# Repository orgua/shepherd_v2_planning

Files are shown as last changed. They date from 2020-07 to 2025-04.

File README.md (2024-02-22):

# Shepherd V2 - Documentation of Planning and Execution




**Main Project**: <https://github.com/orgua/shepherd>

**Main Documentation**: <https://orgua.github.io/shepherd>

**DevLog-Documentation**: <https://orgua.github.io/shepherd_v2_planning/>

---

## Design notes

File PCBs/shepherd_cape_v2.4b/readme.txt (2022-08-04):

Umfang:

- 15 Baugruppen / PCBs 
	- wenn möglich 1 PCB Bestückung als Testsample und den Rest 2-3 Wochen später nach Freigabe
	- falls für die letzte Platine wenige Bauteile fehlen, dann gerne unvollständig bestücken
- 350 Bauteile, 50 unique
- einseitige Bestückung
- smallest part: 0402 
- smallest pitch: 0.5 mm
- only top layer populated
- Bestellung notwendig, nicht alle Bauteile konnten beigestellt werden (siehe Unten)

Platinenfertigung / Manufacturing Constraints:

- Designdaten befinden sich im Anhang
    - GerberX2-Datensatz
    - BOM und Packliste für SMD-Teile
    - Pick and Place Koordinaten für SMD-Teile
	- Assembly-Drawings
	- schematics und Platinenrendering

- PCB-Size ist 54.1 x 75.2 mm, 6 Layer
- Koordinatenursprung ist außerhalb des Boards, links unten

- Standard Eurocircuits / Betalayout Designrules
    - 0.15 mm Track Width
    - 0.15 mm Copper Clearance
    - 0.38 mm Edge Clearance
    - 0.35 mm Toolsize / non plated Hole
    - 0.25 mm Plated Hole (End-)Size
    - 0.125 mm Annular Ring
    - 2.54 mm Milling radius
	- beidseitiger Bestückungsdruck
- Stencil: Solder Paste Pads are optimized for a 70 - 110 um Stencil

- markings: 
	- Mech-15 contains assembly notes / Pick and Place 
	- marking origin of part: cross (+) on assembly notes layer 
	- marking pad 1 of ICs: chamfered edge and circle (assembly notes) and filled triangle (silk) 
	- marking cathode of diodes: "C" or chamfered edge (assembly notes) and filled triangle (silk) 
	- Mech-2 contains Top Part Designators 

BOM / Bestellung:

- BOM hat rechts Spalten für Info über beigestellte und fehlende Bauteile
- Bauteile können durch den eigenen Bestand ausgetauscht werden, falls es den Prozess vereinfacht
- fehlende oder nicht ausreichende Bauteile bitte Nachbestellen

Difference in B-Version of v2.4

- adapt to mouser-stock 
	- Pitch: avoid .35 mm , now it's >= 0.5 mm
	- Solder Mask Sliver: now safer > 0.2 mm

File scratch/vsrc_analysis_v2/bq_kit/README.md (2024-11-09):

# Characterizing the BQ25570 Eval Kit

## Setup

Components described from front to back

- Elgato Key Light in white Light Box
	- controllable by percent-value
    - first run: 5 %, 10 %, 15 %, 20 %
    - lowest: 3 %
    - second run: 4, 6, 8, 10, 12, 14, 16, 18, 20, 22
- Solar cells in same box, exposed to the LEDs
	- model: TBD
    - VOC-MAX ~ 3.18 V
- BQ25570 with said solar cells as input
	- BQ25570 Eval Kit (Modded as described below)
- resistive load on output of buck-converter
	- Open Circuit (OC), 1k (cherry-picked, spot on)

## Measurements

- ivcurves of solar cells, recorded with shepherd harvester @ different light levels
- Saleae Logic Pro 16 (2MOhm Impedance) was used to record analog pins of BQ-IC
    - 31 kHz sampling rate 
	- V_IN - output of solar cell, input of BQ
	- V_BAT - (==V_STOR) voltage over storage capacity on Eval Kit
	- V_Out - output of buck-converter, input of load
- BAT_OK signal was recorded digitally by the logic pro
	- BAT_OK is also enable-signal for buck-converter of BQ

# Changes to the BQ-Eval-Kit

- lowering the VOC of the solar cell -> one cell, not two in series
- adjust the V_Bat over-voltage limit to ~ 5.25 V (5.5 is the theoretical max)
  - the capacitor is rated for 6.3 V
  - VBAT_OV = 3/2 * VBIAS * (1 + R1/R2), VBIAS = 1.21 V
  - 4.18 V setup: R1 = 7.5 M, R2 = 5.76 M -> EVM-Default
  - 5.00 V setup: change R1 = 10 M -> violates BQ-Req that R1 + R2 < 13 M
  - **5.22 V setup: change R2 = 4 M (preferred, 2x 2M)**
- adjust hysteresis of Bat_OK to 4 to 4.5 V
  - default: 2.79 V to 2.99 V for BAT_OK = ON
  - BATOK-PROG = VBIAS * (1 + R7 / R8)
  - BATOK-HYST = VBIAS * (1 + (R6 + R7)/R8)
  - default: R6 = .887 M, R7 = 6.98 M, R8 = 5.36 M
  - 4.03 to 4.38: change R8 = 3 M
  - **4.03 to 4.43: change R6 = 1 M, R8 = 3 M (preferred)**
  - 4.03 to 4.83: change R6 = 2 M, R8 = 3 M (showed some unwanted effects)
- enable output with BAT_OK (enable JP6)
- directly connect V_STOR = V_BAT (bridge the Mosfet)

- Setpoint: on-off-behavior should be present
  - double solar cell @ LED900mA can produce 4mW, so one cell should bring 2 mW
  - 1 kOHms at 1.8 V draw 3.2 mW (most interesting)
  - 100 Ohms at 1.8 V draw 32.4 mW

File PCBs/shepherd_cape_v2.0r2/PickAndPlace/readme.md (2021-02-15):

InCircuit 
Wanted format: http://wiki.in-circuit.de/index.php5?title=Format_Maschinendaten

- Bestückung von 30 PCBs, einseitig, alles SMD (minimal 0402, QFN, nichts exotisches)
- PCB-Maße sind 55x75 mm mit zusätzlichem umlaufenden Nutzen, 10 mm
- 292 Bauteile, 40 Unique (volle Version)
	- 235 Bauteile, 40 Unique (ohne Recorder / Linker Shield + Teile Links davon)
- Koordinatenursprung ist nicht die linke untere Ecke der Platine, sondern 11.176 mm nach links verschoben
- Bauteile werden von uns gestellt, leider nicht im Reel
- R/C-Standardbauteile können gerne ersetzt werden durch Ihren Bestand, falls die bestehenden Reel wirtschaftlicher verwendet werden können als unsere Bauteiltüten 
   - falls es Toleranz-Anforderungen gibt, sind sie bei Value notiert
   - 173x 0402-Bauteile könnten in Frage kommen

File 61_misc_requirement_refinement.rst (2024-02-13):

Requirements Refresh / Refinement 2022-06
=========================================

(rough version)

- more focus on a general testbed for the Internet of Things, especially:
- GPIO Monitoring -> higher min sampling frequency / guarantees
	- nRF and MSP430 have 16 MHz baseclock -> same region would be nice
	- chip-rate of 2 MChip/s,
	- 200ns per loop == must, 150 ns == nice, more welcome
	- idea: state-machine triggered sampling with max window size (example: target uses one pin to trigger sampling for 50 ms)
- UART Monitoring (RX from Target-Side), min 461 kBaud, better 922 kBaud (1MBaud maybe easier)
	- software defined, linked with GPIO-Monitoring
	- timestamp with 1ms-resolution is enough, whole line, start of transmission
	- more detailed timestamps are often embedded in message itself
	- document wrap (if needed), for someone that uses no \n\r, OR
	- OR user-defined wrap-symbol
	- test for ascii control chars (storage in h5 and csv-file) -> or document forbidden chars
		- also base64, 85, 91, or raw
	- continuous stream should also be functional (1MBaud, long duration, creates 10Mbyte stream currently -> might be a problem) -> specify max rate if not possible
- actuation (like UART-Sending):
	- telnet seems not useful (tests can run at night, )
	- top-feature: script on observer with additional logic would be nice (read and write gpio / uart)
	- nice-feature: config-file with time-based send-commands
	- min feature: gpio-actuation per PRU, synced
	- idea: state-machine preload, without reads during run,
- lower sampling bounds should be guaranteed and known -> avoid spurious phantom signals
- Sync-Error should be lower than Clock of GPIO-Register of target

     - Example: 1 / 16 MHz -> 62 ns

- GPIO Actuation, set predefined pins, precise between nodes, resolution can be rather low (100 kHz more than enough, even 10 Hz could be enough), parameters:

    - t_offset (since start of measurement)
    - node(s)
    - GPIO(s)
    - State

- GPIO Actuation for Live View could be beneficial (users can check if system is alive, but what else?) (only nice to have)

Thoughts on Feasibility
=======================

GPIO Monitoring

- with constant voltage (only current-monitoring, no virtual source model) one PRU-Core would be idle -> custom firmware
- PRU0 handles monitoring el. current, actuating GPIOs, Sync timebase, exchange data-buffers
- PRU1 handles only GPIO-Monitoring -> busy waiting

UART Monitoring

- current design routes UART to ARM controlled Pins (Linux) and PRU (GPIO Monitoring, discrete timestamped Events)
- Linux UART RX will be tested -> we are currently stuck at kernel 4.19 but have to switch to 5.10+ eventually
- for PRU monitoring the dedicated section applies

Sync-Error

- there is still a low frequency with unknown origin (~ 0.2 Hz)
- current limits are hard to improve
    - error between nodes: +- 400 ns abs, q95% ~ +- 200 ns
    - error between local triggers: ~ +- 120 ns abs, q95% ~ +- 50 ns
- tbd: deployed cisco-switch in TUD has layer 3 routing and >doubled spec -> could improve sync

TODO
====

- implement enablers / general improvements

    - decouple GPIO-Ringbuffer from IV-Stream-Buffer -> size constraint of 16k Events per 100 ms
    - current buffer-swap implementation is not optimal, takes too much time and should be replaced by a big ring-buffer -> makes mutex between PRUs redundant

- test UART RX with kernel 4.19 / 5.10 with 461 and 922 kBaud
- fork PRU-Firmware with focus on GPIO-Speed

    - test capabilities

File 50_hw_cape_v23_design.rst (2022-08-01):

Shepherd Cape v2.3
==================

Changes Done for v2.4
---------------------

- Power Analog-Switch U30 from BB 3V3
- stabilize ADC with 22 pF at Input -> 60 kHz Fc
- stabilizing 1kOhm for VIOBuffer
- decide if rec & emu should be combined
    - more complex design
    - always complete package
    - reduced cost (~ 3*9 €)
    - emu gets voltage-measurement for free
    - -> no for now
- ADC seems to act up sometimes after sheph-EN -> test in PRU, reenable a couple of times -> seems to be fixed with EN
- Pwr-by-BB does not work with current cape-revision -> just add a switch?
    - switch for input power, 1 A, 5V Switch: https://www.mouser.de/ProductDetail/Dialog-Semiconductor/SLG5NT1594V?qs=sGAEpiMZZMtxrAS98ir%252BsxAQ5ATuKOGcAYPhn0zy8SaYiCqL8FxMXA%3D%3D
    - test shows that the unpowered watchdog is responsible -> add another diode to also power WD from BB 5V OR power diode directly from middle-pad of 2-WayJumper
    - tests still show unreliable starting-behaviour when BB-Pwrd (start on second try), hints at trouble with big coil & Cap -> also implement the switch
- remove overvoltage-protection, due to space constraints
- ditch LSF-LevelTranslator, use 74LVC2T45DC,125 with directed pairs
    - 74LVCH2T45GT, holds, 1.0 * 1.9 mm Package: https://www.mouser.de/ProductDetail/Nexperia/74LVCH2T45GT115?qs=jquClx72t9BCfx5QcUZHzg%3D%3D
    - 74LVC2T45GN, without hold, 1.2 x 1.0 Package
    - 74LVC2T45GS, without hold, 1.35 x 1.0 Package -> cheaper, more available
    - 4x100k-PU Array https://www.mouser.de/ProductDetail/YAGEO/YC124-JR-07100KL?qs=o9qB%2F%252BVTi4WdZhClKs2MsA%3D%3D
- programming biDir Pins
    - var1: skip leveltranslator and force 3v3 logiclevel, direct connection with analog Switch
    - *var2*: that one pin tdio must have a dir-pin -> hard if PRU-Pins needed
    - var3: still use slow LSF0104 for programming pins (try TI-Version for a change)
    - -> var2 is preferred if sys-gpio is working for programming, (YES, it is)
- GPIO to target, 7x GPIO, 2x UART (rx,tx), BAT_OK (tx)
    - how many gpio should be with variable direction? 2x2 rxtx, 5 static rx? ->
    - static-Dir TX: CLK1, TMS/CLK2, BATOK -> 2 x 2 CH Translator
    - static-Dir RX: UART-RX, 4x GPIO, -> 3 x 2CH-Translator
    - BiDir: TDIO1, TDIO2, UART-TX, 3x GPIO (4 Dir-Controlling Pins, 2 for programming, 2 for tx&GPIO and 2-4xGPIO)
        -> could be bundled in TDIO/GPIO-Pairs for a 2 x 2CH-Translators (NO)
        - if possible don't share Dir-Pins between programmer / gpio
- possible extension of target port
    - programming pins are exclusive and don't have to be recorded/monitored -> free pins should be used for additional gpio
    - a second target (with option of programming) would help for some usecases (MSP430 + nRF-Radio)
    - var1: analog switch on target-pcb for programming lines controlled by one of the gpio (exclusive or could still be used as gpio)
    - var2: analog switch on cape, 2x2 programming lines on target-port, also allows JTAG
    - var3: intermediate uC on target-pcb for programming targets talking with BBone over programming lines (very custom solution but cape is left untouched similar to var1)
    - -> Var2 preferred
- WD-Wake needs longer Pulse
    - currently 20ms High-Pulse gets inverted, but tests show that > 130 ms are needed
    - var1: diode + RC-Filter could widen the Pulse
        - wake-pin supplies 1mA max
        - SIM: 100 nF / 1 M -> 150 ms > 0.5V (On for MOSFET)
        - SIM: 1 uF / 1M ->  >>1s > 0.5V
    - var2: a single capacitor after the mosfet could suffice
        - BB-Schematic only shows a pull-down button
        - TPS65217C, PB_IN, Pin25, internal 100k PU
        - SIM: 1 uF from BB-START to GND shows 100ms delay for signal rise to 2.0V -> sums to 120 ms
            - ~ 64ms in real test
    - -> Var1 preferred, less dependant from BB-Design-Changes
- PUs on sys-side should also be powered by BB 3V3
- New Connector, 4x Pwr, 4x Prog, 10x GPIO -> 18 Pins -> 2x9 Connector
    - info1 -> BB outer width is 54 mm -> 27mm per module
    - info2 -> BB width between headers is 43.2 mm -> 21.7 mm per module
    - var1: remove mounting-holes and allow 2.54mm Connectors (2x 22.2 mm width)
    - var2: switch to smaller 2mm Connector, ~18mm width
    - -> var1 preferred
- GPIO-PUs increase to 100k
- combine shield-pads for EMU & REC
- change Analog switch to microbump-version 863-NLAS4684FCT1G
- change back vias from 550/200 to 600/250
- add more decaps for level-translators
- Remove dedicated harvest-led -> use pru0-LED for that

Changes still Open
------------------

- which rails would benefit from big Caps?
- emu-shunt should be stabilized with > 500 nF (and probably the others too)
- additional big Caps on Main-Rails
- Resistor Arrays?
    - 4x 100k https://www.mouser.de/ProductDetail/YAGEO/YC124-JR-07100KL?qs=o9qB%2F%252BVTi4WdZhClKs2MsA%3D%3D
    - others1 https://www.mouser.de/c/passive-components/resistors/resistor-networks-arrays/?resistor%20values=100%20kOhms&instock=y&sort=pricing
- Beta Tuning:
    - additional 1 nF Cap on Feedback LP, both paths
    - remove 100 nF parallel to shunt
    - give recorder equal layout
- optimize filters with noise-metrics
    - possible tradeoffs: speed of voltage-transitions, compensation of analog switch resistance
- finalize hardware (WD, filters, GPIO-Speed, current bugs)
- test harvesting-target
- get target naming A/B/1/2 straight. it is target 1/2 from now on!
- find reason for 2.3mA Offset
- diodes for coils if needed
- LED of PRU: dedicated pwr_good / harvesting on silkscreen

Trouble with v2.3c - manual P'n'P
---------------------------------

Fixed in v2.3d

- better comments for parts, U- , L-, R-.... T-
- SLG5... 4pin-mini-package, improve pin1-point and pad-layout should be hinted at ->
    - also longer pads,
- optimize NLAS-BGA, silk-lines, maybe extend corner-pads, peek over ic-edge or add right angles in copper
- 74LV LVLTrans - longer pads, at least the 4 corner ones -> maybe one package larger
- 0402 pads closer together
- u14 pads further apart
- the 3 new ICs -> maybe back to larger package?
    - 74LV as QFN, end-of-life: https://www.mouser.de/ProductDetail/Nexperia/74LVC2T45GM125?qs=sGAEpiMZZMtZ661ya8CuXWImkGMxfA6p9uS%252BIOJA%2FTA%3D

- 1 C tombstone (below emu, above u19)
- level-trans seem to be shorted (densest pad-layout)
- some ICs are shorted -> old paste

Additional Parts
----------------

- 22pF for Emu-ADC
- 1k Ohm VIO-Buffer
- 9 74LVC2T45GS -> 2CH LevelTranslators
- 1x SLG5NT1594V -> 1A Power-Switch
- EN_CONV: R 10k, C 1uF
- WD: 2x NSR05T30XV2T5G, R 100k, C 1uF
- LVL-Trans: >20x 100k, 5x 1uF
- AnalogSwitch: 9x 863-NLAS4684FCT1G
- pinheader 2x18, 2x 649-1012938191801BLF

Parts not needed anymore
------------------------

- OVP: 2x FB 0603, C 22 uF, R 10 k, Mosfet BSH105, Diode NSR05T30XV2T5G
- WD: R 10k

Target Pin Design
-----------------

- GPIO 0            - dir1-pin / rxtx
- GPIO 1            - dir1-pin / rxtx
- GPIO 2            - dir1-pin / rxtx
- GPIO 3            - dir1-pin / rxtx
- GPIO 4            - always RX
- GPIO 5            - always RX
- GPIO 6            - always RX
- GPIO 7 - uart rx  - always RX
- GPIO 8 - uart tx  - dir2-pin / rxtx
- BAT OK            - always TX

- SWD1 CLK - jtag TCK   - always TX
- SWD1 IO  - jtag TDI   - pDir1-pin / rxtx
- SWD2 CLK - jtag TDO   - always TX
- SWD2 IO  - jtag TMS   - pDir2-pin / rxtx

PinChanges from prior Version v2.2 to v2.3
--------------------------------

see `./PCB/beaglebone_pinout_concept.xlsx` for more details

Changes

- p8-27 was pru-gpio4, now pru-uart-tx
- P8-39 was pru-gpio2, now pru-gpio6
- P8-40 now pru-uart-rx
- P8-41 now pru-gpio4
- P8-42 now pru-gpio5
- P9-17 only naming, swd1_clk
- P9-18 only naming, swd1_io

New

- p8-31 / 32 now used for io-dir
- p8-33 sw_swd2_io
- p8-34 sw_gpio6
- p8-35, 36, 37, 38

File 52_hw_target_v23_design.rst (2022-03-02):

Target with nRF52 and MSP430
============================

Changes still Open
------------------

- new Target-Port
- wider PCB allowed, BB-Heigth is 54.1 mm -> half is max 27 mm
- TargetPCB: are there constraints or feedback for the MSP430 + NRF - Combination
    - Which IC would you prefer?
    - example-schematic for the combination available?
    - IC interconnect: SPI (4 Lines), 2+ handshake-lines (Project Squeece)
    - Target-Connector-Gpio access for both uCs?
    - TODO: use nRF TRCDAT0 / P1.00 / on Target header
    - Github / squeece
- target -> add target powered LED to burn away energy (or use second LED for that purpose)
- nice to keep similarity to DK, but not a must
- Squeece Pin-usage
    - C2C CLK,  P0.13,  P1-6_UCA0CLK
    - C2C MOSI, P0.12,  P1-4_UCA0TXD
    - C2C MISO, P0.16,  P1-5_UCA0RXD
    - C2C CS,   P0.15,  P1-7_UCA0STE
    - C2C GPIO, P0.14,  P2-7_CAP3
    - nrf-gp0   p0.17
    - nrf-gp1   p0.19
    - nrf-gp2   p0.28
    - nrf-led   p0.29
    - msp-gp0           P2-1_XIN
    - msp-gp1           P1-1_UCB0CLK
- MSP430 Variants
    - MSP430FR2433IYQWR -> BGA-Version, 16 kB FRAM
    - **MSP430FR5964** with 87 Pins, 256 kB FRAM -> there is an 48 PinVersion FR5994, even 59941 is ok
    - MSP430FR5992IRGZR , 48 Pins, 128 kB FRAM
    - or MSP430FR2155 with 32 kB and 48Pins and 32 MHz -> PinCompatible?
    - SPI to Target, seconds SPI to nRF
    - prepare to equip both crystals (HF, LF)
    - eine der eUSCI Schnittstellen (sind beim MSP hart verdrahtet) soll richtung BB gehen. Und der eine pin davon (z.B. UCA0RXD/UCA0SOMI) muss auf BB richtungsschaltbar sein.
- msp430
- shared pins are working fine on squeece, ~ 10nA draw on high impedance
- add star-resistors
- programmer - compensate lines with passive network

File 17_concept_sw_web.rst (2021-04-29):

Concept - Software - Web Interface
==================================

MetaInfo
--------
- derived from requirements, concept_shepherd and concept_meeting_notes

Design-Features
---------------
- Privacy is a features - avoid personal data (OAuth, ActiveDirectory)
- usage per website & API
- 1 experiment at a time, no concurrency

Functions
---------
- user-management
    - permission
    - role management
    - groups (share datapool)
    - Quota (data is linked to user and deleted with the account)
- authentication via external service like OAuth (i.e. Github) (if possible)
- Upload user provided data
    - Harvesting- / Energy-Traces, -traces, IV-Curves
    - regulator / converter-definition
    - Target-Firmware
    - user-scripts (sandboxed, limited resources (cpu, ram, storage), only limited libs allowed, limited user, lowest nice-level)
- Scratch-Area for experimentation-results (or DB)
- integrated pre-tests for measurement: test for plausibility, pre-run in software (abstract virtual hardware)
    - link in python code of shepherd project
- scheduler for measurement, time to prepare and follow up (data transfer, conversion, compression, ...)
- results downloadable by user, for a certain time (no hording)
- feedback via e-mail - measurement start, data available, error, shortly before deletion
- (optional) grafana-visualisation
- documentation and instructions
    - landing page
    - "what is that thing in my office"
        - clarify use and capability of the boxes (so people sharing an office with the testbed don't freak out)
    - where find what
    - FAQ
- Testbed-Status
    - structure
    - last seen
    - handle lockups (power-cycle)
    - keep testbed alive for a limited time (otherwise it will go to sleep / power down)
- collecting of logs (temp, ram-usage, cpu-usage, time-sync, ...)
- Web-Framework (some points are redundant)
    - user-management (roles for admins and users)
    - experiment-management, configure and control, add data (see below)
    - experiment-scheduling, calender (set active, start-time, duration)
    - data management / quota (retrieve / delete recordings)
    - authentication via external services
    - E-Mail notifications
    - testbed status, topology
    - (optional) grafana visualisation of recorded data
    - (admins) server status, quota, testbed control
    - documentation and instructions
    - target-management (specify slots of nodes)
    - (optional) benchmark-management (post-scripts)
- live-view -> lower prio

Implementation
--------------
- possibly python based (django vs flask, big vs small)
    - django offers the most, is flexible, modular and easy to extend
        - admin-interface
        - authentication (also oauth client), accounts
        - session-management
        - sub-websites with html-templates
        - -> security seems to be OK, attach surface is big, but >v3.0 seems to be mature
    - flask is a microframework, offers minimal attack surface and seems perfect for the python REST API
- basic implementation could be similar to https://github.com/fkt/36c3-junior-ctf-pub (web-interface for a ctf, that didn't get compromised)
- API: rest
- (prio) allow scripted workflow -> yaml -> rest ->
    - this could also be the base for the web-page-interface
- Database
    - influxDB or
    - timescaleDB
    - postgreSQL
- MessageSystem
    - Protobuf
    - RabbitMQ
    - RPC
- visualisation, analysis -> dash?
- option to sample down

DB Decision
-----------
- needed:
    - 30x 100k Inserts of timestamp (8B), node_id (1B), voltage (4B), current (4B)
    - -> 3M Inserts of >=17 Bytes -> 3 GB / minute
    - can happen locally or remote, concurrently is fine
- main bottleneck:
    - databases with timeseries do not seem to have a low level api for insertions, interface is ascii and needs parsing
    - (solution) low level api (raw data, shared mem, ...) -> there are possible formats like::
        - BSON -> MongoDB
        - UBJSON -> TeradataDB, Wolfram (no use for us)
        - apache avro -> Apache Spark SQL
        - JSONB -> Postgresql, but they say: "JSON is faster to ingest vs. JSONB"
- Timescale DB vs Influx -> influx seems to dominate with fewer devices <= 100
- timescale: SQL, robust, based on postgreSQL, time series, relational, various datatypes
    - looks more professional, but like influx they want to sell
    - presetup hard to script
    - 1M insert/s are considered excellent, i landed at ~60k with one remote connection
    - no low level api available, but some SQLs allow to load from file (csv)
- influxDB2:
    - inserting 200s data takes ~ 190s (1 node), with almost no load on VM or system
        - -> makes 108k/s inserts from one node
        - marketing documents say the insert-rate of free-database is good for ~ 250k/s
        - is it artificially limited or is it another invisible bottleneck?
    - ram usage seems to be ok << 1 GB
    - query's with ns resolution can get very slow. ~3s for averaging windows
    - influx can almost naturally import hdf5, numpy-arrays, pandas Dataframes
    - dataexplorer shows plots only windowed, smallest window is 1s (may be unimportant)
- elastic + logstash, search engine,
- redis, key-value store
- mongoDB
    - allows usage of BSON instead of JSON

DB-Bypass
---------
- measurement-data could be stored directly on the server
- each measurement is stored in a separate folder, named by hash or timestamp
    - it contains config data, logs and results
- file-references are inserted into a DB
- metrics for benchmarks or competitions could be generated by a user-script
    - pandas or numpy, as a fast cPython convenience, allows powerful oneliners
    - these metrics could be displayed on the website as a condensed result
    - these metrics could also be used for some kind of leaderboard
- a downsampled dataset (1 kHz?) could be fed into a database for semi-live analysis / observation
- a full-res dataset could be fed into the database afterwards but would mean a longer blocking time between measurements

TODO
----
- try payed db-vm (influx)
- compare elastic against influx, no support for nanosec?
- benchmark server (disks / ram)
- offer predefined energy-patterns (on/off, diode, different converters (boost, buck/boost))
- design-choices for later
    - does shepherd need databases for immediate (deep)analysis of result
        - alternative: provide post-scripts that filter data for key-parameters (benchmark-management)
    - data hording or economical use of space?
    - what else ?????

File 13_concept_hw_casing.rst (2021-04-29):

Hardware Casing for Nodes
-------------------------

Constraints
-----------
- nodes can vanish, wander
    - fixate
    - keep inconspicuous (under desk an option?), make it look official / blend in
- nodes can freak out new people in the same office
    - must look professional, official
    - be transparent about the function (inform current people in office, but also use sticker to provide a FAQ-Website
- must support cooling (direct sunlight, proximity to radiator)
    - convectional cooling would be the easiest
- must contain
    - BBone with shepherd Cape (75 x 55 x 25 mm)
    - POE-Converter (81 x 55 x 25 mm)
    - Target nodes (20 x 30 x 4 mm) - orthogonal on capelet or in direction of longest edge of capelet)
    - < 20 cm Network cable
    - power-connection
    - USB-Stick (45 x 20 x 9 mm)
    - opening for one RJ-45-Socket
- must be transparent to RF
- input Marco:
    - open and transparent is fine and wanted (!)
    - boxy is ok
    - preferable hard mounted to the wall with just one cable attached

Layout
------
- flat on one level
    - X: 75 + 45 + 30
    - Y: 55 + 55
    - Z: 25
    - 150 x 110 x 25 (412 cm²)
    - pro: clean,
    - contra: harder to cool, less optimal RF-performance (antenna near to ground)
- Stacked
    - X: 75 + 45
    - Y: 55
    - Z: 25 + 25 + 30
    - 120 x 55 x 80 (528 cm²)
    - pro: more boxy, would better fit ontop of the cable canal
    - contra:

Solutions
---------
- 3d-Printing
    - flexible and custom case
    - way to expensive for 30 Nodes
- Casing in laser-acrylic or plywood
    - solid, custom
    - may look also unprofessional, like a building kit
    - design without screws -> https://hackaday.com/2013/02/27/acrylic-enclosures-use-integrated-clips-to-do-away-with-fasteners/
- off-the-shelf case with custom front
    - can look professional
    - you have to take what the market offers
    - way around custom front is: just include an opening for the cable with a gasket (or right there where two halves meet)

Off-the-shelf Cases
-------------------
- flat (25-35 height, 150-183 length, 110-135 width)
    - https://www.mouser.de/Enclosures/_/N-5g3o?P=1yzti4fZ1yzxi2vZ1yzu1qgZ1yzxiszZ1yzu1na&Rl=5g3oZer8qZ1z0wu34Z1yzsnvlSGT5g3oZer7lZ1yzxi96Z1yzxi5vSGT
    - hammond 1599TABMBK / GY, 28 x 135 x 169 mm with custom cover, hardware can be mounted inside with laser-cut brackets
        - https://www.hammfg.com/electronics/small-case/plastic/1599tab
    - hammond 1557FGY, 160x160x45, no option for cover
        - https://www.hammfg.com/electronics/small-case/plastic/1557
    - hammond RM2055S
        - https://www.hammfg.com/electronics/small-case/plastic/rm2
- stacked (120-140 length, 55-75 width, 80-125 height)
    - https://www.mouser.de/Enclosures/_/N-5g3o?P=1yzu1tfZ1yzu1f6Z1yzu1ggZ1yzsn9pZ1yzoes7Z1yzxin2&Rl=5g3oZergvZ1yzu1ffZ1yzxigsSGT5g3oZer8qZ1y8pz55Z1z0wu4tSGT
    - Bud PTS-25312-C, 5.12x2.76x3.15"
    - Hammond 1554G2Gy, https://www.hammfg.com/part/1554G2GY
    - hammond 1555, https://www.hammfg.com/part/1555G2GY
    - hammond RP1150C, https://www.hammfg.com/part/RP1150C
    - hammond rp1155, https://www.hammfg.com/part/RP1155

Favorite 1599TABMGY
-------------------



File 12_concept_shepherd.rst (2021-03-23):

Shepherd - Concept
==================

Overview
---------
- (mobile) testbed for batteryless IoT
- observer-nodes for an IoT-Target
- works autonomous or time-sychronized with a network backplane
- "software defined power source", emulation of
    - harvesting source (pre-recorded, simulated)
    - regulator / converter - circuit
    - intermediate storage-capacitor
    - "software defined" is largely true, but changing basic behaviour needs a deep dive into PRU-Code
- allows to experiment with emulated spatio-temporal energy availability
- recording of energy-traces -> key-parameters like current-drain and (virtual) capacitor-voltage
- additional functionality: recording of harvesting sources (not part of testbed)

Nodes
-----
- embedded linux board with shepherd-cape
- time critical code runs on two real-time processors
- two targets-ports are available
    - both can be supplied with individual voltages, only one is current-tracked
    - general purpose IO, target selection independent from power-supply-selection
    - separate 3V3 line
- bidirectional GPIO on 10 channels, 2x2 lanes are currently reserved for SWD / Spy-by-Wire, UART
- Targets (currently planned)
    - nRF52840
    - MSP430

Testbed
-------
- 30 Nodes on one floor in a university office-building
- nodes powered via POE
- (optional) one PTP-Masterclock, Node with GPS
- 1 Ubuntu Control-vServer, 10 TB of additional Storage
- 1 experiment at a time, no concurrency
- Web-Framework
    - user-management (roles for admins and users)
    - experiment-management, configure and control, add data (see below)
    - experiment-scheduling, calender (set active, start-time, duration)
    - data management / quota (retrieve / delete recordings)
    - authentication via external services
    - E-Mail notifications
    - testbed status, topology
    - (optional) grafana visualisation of recorded data
    - (admins) server status, quota, testbed control
    - documentation and instructions
    - target-management (specify slots of nodes)
    - (optional) benchmark-management (post-scripts)
- user-provided data (experiment management)
    - (optional) energy-traces, IV-Curves
    - regulator / converter-config
    - target-firmware
    - (optional) python userspace script that interacts with gpio / serial

Technical details
-----------------
- Beaglebone Green with 1 Core for Linux and heavy use of PRU for low-latency code
- target-voltage 0 to 4.5 V, max 50 mA per Target
    - 16 bit DAC, LSB results in 76 uV
    - 100 kHz sampling rate, jitter max +- 90 ns, 95% Quantile is 60 ns
    - 18 bit ADC, LSB results in 19.1 uV or 191 nA
- speed of voltage-drive
    - DAC has 0.75 V/us slew and 7 to 10 us settling (error < 0.x %)
    - OpAmp has 5 V/us slew
    - following Lowpass has corner-frequency of 16 kHz
    - 10 kHz on-off-patterns should be well in range
- low noise & high precision design for analog frontend
- 10 shared GPIOs with system
    - bidirectional level translation works from ~ 1.3 to 5 V
    - line is driven by PUs, always matched to target-voltage (low power usage)
    - recording: sampling rate is asynchronous, between ~ 1 to 5 MHz
    - data throughput untested, but edges look fine for > 1 MBaud
    - leakage during operation < 2 uA from target-side
    - gpio can be turned of, < 10 nA leak from target-side
- data-rates
    - 1 min ~ >= 54 MiB of measurement data (more with heavy GPIO actions)
    - 1 Hour, 30 Nodes -> 100 GiB uncompressed (hdf5)
- time-synchronization
    - in linux via PTP,
    - chip-select edge of two test-nodes have a maximum jitter of about +- 300 ns, 95% quantile is 160 ns
- external watchdog for wakeup / restart on
- network
    - Server has 10 GBit Link to Switch
    - Nodes have 100 MBit Link to Switch

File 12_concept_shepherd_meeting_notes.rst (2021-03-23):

Learnings, with Pitfalls and (possible) Solutions
=================================================
- notes from meetings with creators of established testbeds
- significance for shepherd is incorporated

Server
------
- have an upgrade path
    - currently TUD/ZIH offers vServers and plenty of Storage from its datacenters, can be changed, expanded
    - current server: 2 Cores, 4 GB RAM, 50 GB local Storage, 10 TB network storage
    - vmware-tools have option to set cores and ram to 64 (for privileged users)
- avoid windows OS
- splitting servers can be an option (storage with message broker, web-interface, computing)

Data-Management
--------------
- database (not a must)
    - allows easy analysis of data
    - immediate access is nice! real time or direct access for devs (even jupyterNB)
    - needs lots of RAM
    - easiest interface is a socket with json-interface -> inefficient for embedded systems, can often be avoided
    - can produce downloadable data on the fly (at least csv)
- hdf5 / raw-data
    - needs more custom code
    - analysis not available right away
- database-choices
    - influxDB allows nanosec-timestamps as a series
    - postgreSQL works for weeks
    - timescaleDB, inlux competitor, seems to scale better with large number of devices (>1000)
- leave headroom, node-resources can easily become the bottleneck
    - using third party libs is always a good idea, but can come with performance penalties
    - usually compute-load can partially be moved to server
    - there are often performance optimized forks of established libs around (if needed)
- established ways / libs to stream data out
    - protobuf (can be slow for python)
    - rabbitMQ / kombu
    - RPC
- is privacy is feature? avoid personal data (OAuth, ActiveDirectory), make recorded data private (even only delete-access for web-admins)
- grafana seems to have trouble with big datasets

Nodes
-----
- lockups -> powercycle
    - we (shepherd) may not have the chance to control POE
    - there is an external watchdog on the shepherd-capelet
    - there should also be a watchdog integrated in cpu (untested)
    - until now i (ingmar) had no trouble with the nodes, software base seems solid
- heat through sun, radiators, enclosure
    - degrades cpu, storage
    - BBone stays below 40 deg, case will support convectional cooling
- avoid storage without wear-leveling
    - sd-cards are not up for constant data-storage (and industrial SLC-Versions are expensive)
    - large usb-sticks tend to have wear leveling -> ours probably hasn't
    - BBone has eMMC for the linux image, support for wear leveling is unclear
    - filesystems like F2FS have a software-based wear-leveling
    - possible solution
        - keep results in ram (avoid local storage bottleneck) and stream to server
        - use usb-stick for local storage of energy-traces (more static data)
        - keep system read-only (only deactivate for updates)
        - have replacement BBones at hand (automate installation)
- collect logs
    - gives debugging-hints in events of unwanted behaviour
    - temperature, ram-usage, cpu-usage, ...
- target repurposing
    - keep functionality general so it can be used for dev, testing, ...
    - shepherds nRF-Target already has more gpio on edges and optional usb-port
- alternative platforms (copy from 11_concept_hw)
    - zynq (arm-cores + FPGA + shared mem)
        - pro: similar price as BBAI, 1 GBE, FPGA in same Package, hw-timestamping
        - con: xilinx-toolchain, documentation is overwhelming, community small, long dev-cycle
    - embedded amd platform (v2000)
        - pro: compute-power, relatively cheap (>= 200€), fast ethernet, x86-64
        - con: real-time not out of the box, low gpio-count
- slow software controlled GPIO could be a disadvantage
    - sensor and actuator control can have tight timing constraints
    - BBone PRU can also take control over gpio (but this is static / boot time decision)
- observer should always have control over target-reset
    - shepherd can control soft-reset over jtag/swd
    - shepherd can cut power and power-cycle target
    - add resistor bridge just for safety

Web
---
- flask-framework is sufficient (same with bigger brother django)
- user-management should also include groups (to share data-pools)
- experiment-scheduler could be done with rabbitMQ (message broker)

Testbed
-------
- secure against miss-use
    - nodes can vanish, wander
        - fixate the boxes :)
        - make them unobtrusive (glue below desk, non-transparent-case)
        - BUT be transparent about the function
    - user-scripts can get system-access (heavy cpu-load, buffer-overflow, damage linux-partition)
        - put in sandbox
        - limit py-code to shepherd-framework / no other libs
        - run as special user - only essential permissions
        - set to lowest cpu-priority (nice-level)
    - voltage source could destroy hardware
        - gpio- and supply-voltage for shepherd-target are always linked
        - target-pcb has over-voltage-protection
        - experiment-management will check voltage of emulated regulator to match target-constraints
    - sanity-check everything!
    - real world testing required
- maintenance / development can easily occupy 1P full time
- documentation for the next devs

TODO
----
- try to design low maintenance, multi-purpose, high functionality / speed / quality
- Filesystem
    - f2fs for usb-sticks
    - find read-only-switch for system partition
- is there an easy way to integrate a fresh BBone into the system?
- test target-programming with current shepherd design
    - pyOCD could be an alternative
- BBone
    - is cpu-usage really 70% during emulation?
    - do a performance profiling, find bootlenecks
    - raw data could be sent server, less overhead for BB

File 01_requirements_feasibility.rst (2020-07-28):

Feasibility of Requirements
===========================

- this part is looking mainly on the hardware-challenges (software can be adapted later if the hardware is prepared)

Emulation of Capacitor / DC-Converter
-------------------------------------

- Problem: PRU of beaglebone black is currently already quite occupied with measuring and replay of energy-trace, emulation means real time control loop, the PRU has limited capability for that (no division, ...)
- Enabler 1: keep previous hw-design (fall-back), but add switches to bridge converter and cap (one additional pin - does not need to be connected to PRU)
- Improvement 1: optimize PRU-Code, i.e. bitbanging of SPI
- Improvement 2: current beaglebone AI offers two PRU and 2x dual-arm-cortex-M4 cores (price is 122 € instead of 40-60 €)
- Improvement 3: try to find approach where same cape-pinout can be used with beaglebone black and beaglebone AI
- improvement 4: it would be beneficial to make MPPT-Conv & Cap Modular
- assessment:
    - mostly critical is software / firmware implementation
    - -> hardware enabled approach, not difficult in hardware, low risk and low impact on time expense
    - also allows On-Off-Pattern for target-power

More GPIO to Target
-------------------

- Problem1: gpio must be real time in PRU, PRU Pin-count and workload limited
- improvement 1: share programming-pins (currently not possible)
- improvement 2: beaglebone AI offers one more PRU, hopefully with more usable pins
- Problem2: IO in PRU is largely predetermined I or O, decided in device-tree when mapping pins to registers
- solution1: use two pins per PRU to allow IO
- solution2: extend SPI to also talk to GPIO-Extender (would also make level-shifting-easier)
- assessment:
    - PRU has still 9+ unused pins, even 10 (with current ones) in a register-row, but 8 seems like a more suited number
    - PRU should be limited to be gpio-recorder with its pins, a second pin is handled from host

Bidirectional GPIO and fast/variable UART / SPI to Target
---------------------------------------------------------

- Problem: logic signal must be level-shifted and detachable (possible energy transfer) and also high-speed
- current layout: link from Target-GPIO is output only, uart bi-dir & recorded in PRU, programmer is in user space (currently not recordable, dedicated pins on nRF52)
- improvement: change level-changer and switches / muxer if more speed is needed
- solution 1: pru could access spi and uart from host-cpu, has delay-penalty, but gpio from host seems unreachable to PRU
- improvement: PRU could be limited to be GPIO-recorder (see previous requirement)
- assessment:
   - bidirectional gpios will be recorded properly, but never react in realtime if handled in python-api (ok, because main purpose is monitoring)
   - (high-speed) SPI to target is hardly possible, host-periphery and PRU-Pins offen fall together and limit the available pins
   - uart-speeds would allow 192 Mbps with no autobaud and 3.7 Mbps with it

Allow user-provided Energy-Traces
---------------------------------

- assumption: 8 byte timestamp, 2x 4 byte U/I-ADC-Value, 100 kHz -> ~ 1.6 MB/s
- Problem: traces for an hour or day become hard to handle via internet
- improvement 1: allow looping of short sequences (also mirroring for continuity)
- improvement 2: U/I-Values could be partial linear dependent and therefore compressible (data-compression-algorithm, vectorization, delta-conversion)
- improvement 3: beaglebone AI has GBE instead of 100 mbit, that makes data-handling a lot smoother
- assessment:
    - no hardware-changes needed, lib-changes seem manageable
    - traces seem to be compressible by factor 10 to 100 (input Kai), which is fine for playback

Accuracy of time-base
---------------------

- Problem: jitter on gpio-traces from different nodes
- Improvement 1: use ethernet switches with ptp-support, QoS and GPS-Interface
- Improvement 2: GBE of beaglebone AI could bring advantage (faster processing in stack / switch, stricter timing constraints)
- Improvement 3: change crystal oscillators of beaglebone to temperature compensated ones (lower PPMs for drift and aging). Oven controlled crystals would be to big
- Improvement 4: "external" sync signal -> "sync port" is already available for the gps-capelet, and even if it is not used for time-keeping, it can be recorded for later trace-alignment
- improvement 5: ptp has a lot of bad-undocumented set-screws to optimize performance ...
- assessment:
    - no definitive solution for sub 1 µs accuracy, but some of the solutions should be considered in concept phase, others are sw / hw mods in a later stage
    - no risk on hw-level, minimal more time expense in design-stage
    - gpio sampling is already asynchronous @ ~20 MHz

Mobility of Nodes
-----------------

- Problem: node presumably without network access and gps-reception, not powered all the time
- Improvement 1: allow external gps-antenna (not possible for current ublox SAM M8Q / 22 €)
- Improvement 2: offer backup power to gps module, small LiPo or supercap
- Improvement 3: offer software based scheduling and pre-config of measurements on nodes
- Improvement 4: offer a more robust power-connection (micro-USB is bad)
- improvement 5: tweak linux for low power usage (turn off unused devices) and low sd-card usage (disable logging)
- improvement 6: proper casing with interfaces (i.e. eth, power-switch/connector, gps-antenna, pps)
- assessment:
   - low risk on hw-level

Support for other Targets
-------------------------

- Problem: different µC need various programmers
- Info: Flocklab and D-Cube support nRF52 (DFU / USB, SWD), STM32L4 (SWD), MSP430 / 432 & CC430 (JTAG, Serial, USB, Spy-By-Wire)
- Enabler 1: generalize programmer pins and GPIO-Pins to Target (specialize on target-carrier-pcb)
- Enabler 2: bring usb to target device if possible (beaglebone-Pinheader does not have USB, but could be realized via cable)
- assessment:
   - if openOCD supports targets and programming-protocol (or implementing them is doable), chances are good
   - pin-sharing with target-gpio is hard -> device-tree seems pretty static
   - general idea seems viable -> TODO: more reading

Support for two selectable Targets
----------------------------------

- Problem 1: gpios with PRU support are limited
- enabler: relay-switching of targets by beaglebone (not necessarily PRU-Pins)
- problem 2: how to distinguish between ICs automatically
- enabler: software-defined PRU-openOCD could try to probe, get chip-ID with various methods (jtag, swd), similar to JTAGulator
- assessment:
    - hardware changes are fine, board space is not limited (cape can be bigger than beaglebone)
    - software could be more tricky -> py-lib should be "general" (without board-specific config), but target still has to be choosable, and target-firmware has to match the choosen target
    - with some effort even both targets could be powered, one with CV, to allow use as interferer (see next subject) or independent node

Separate RF-Interferer
----------------------

- more specific: controllable rf-standards as interference
- enabler: modules for WIFI and BT could be added per USB / Hub and controlled via linux, defined traffic via iperf (for WIFI) or JamLab-NG
- assessment:
   - should not be main goal for shepherd V2, maybe stretch goal
   - has no influence on cape-hw-design or python-API, can be completely separate (even on extra beaglebone or server)

Channel-Monitoring
------------------

- problem: analog to rf-interferer

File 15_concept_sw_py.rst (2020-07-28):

Concept - Software - Python API
===============================

- lean on interface of established entry-level projects (i.e. wiring, arduino)
- submodules as classes -> basic configuration at instantiation
- lib could be compiled for speed
- do we need exact timestamps for start and stop or is a global trigger enough
- hdf5 for fast storage, data can be segmented into several files, and written incrementally
    - later converters for csv, saleae logic-analyzer-format would be nice
- try to separate between scenario and measurement (reusability)
- individualize target firmware by manipulating ELF-file: tx power and ID/softMAC as variable,
- modules
   - harvesting-emulator: energy-trace(s), sampling-rate, playback (mirrored, loop)
      - or skip emulator by using constant voltage module
      - traces are file based, there will be a default-folder with pre-selected ones (already on beagle)
   - harvesting-recorder: save-path, capture-duration, start-timestamp, sampling-rate
       - includes current-recorder and switch for dummy-load
   - dc-emulation-modul: converter modell parameter, capacitor parameters, pre-charge ...
      - low-level model in PRU
   - target-module: path for trace-dumps,
      - submodules: firmware (+addressing by firmware-manipulation), uart, gpios
      - allow to disconnect all iO (document in logs with timestamp + Event)
- bidirectional GPIO usage
   - allow to pass thread-function to nodes that handle reactions
- start of measurement should be triggered by absolute timestamp and marks T=0
    - what if the absolute time was missed? -> synced start whenever start-signal comes, should be enough
    - after that it seems easier to use relative time increments for controlling submodules
    - interact with cron-jobs or other linux-scheduler
    - currently implemented: absolute time start with scheduler, node needs no control after config

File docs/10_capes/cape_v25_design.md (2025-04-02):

# Cape v2.5 - PCB Changes

Status 2024-02: still not produced - maybe skipped for switching platform

## Implemented Changes v2.5a

- lower current-limiting resistors from 470 R to 240 R (see new target)
- emu U32 replace OPA189 by OPA388
- LP for InAmp AD8421 ⇾ 80kHz with 2x 100R, +2x 1nF to GND
- change invNr-Sys to solid white rect
- Emu - use 10mV Ref directly, without Switch
- Rec - use GND as Ref directly
- stabilize 10 mV ⇾ 1uF increase to 2x 10uF, 2R increase to 10R
- replace electrolytic Caps by MLCC (Optionals on Backside)

⇾ implemented in V2.5a - https://github.com/orgua/shepherd_v2_planning/tree/main/PCBs/shepherd_cape_v2.5a

## Implemented Changes v2.5b/c

- production optimized for JLC
  - 6 layer includes via filling & capping (type 7) -> optional as via in pad is not used
  - vias were reduced to 0.2 mm hole, 0.35 ring dia
- replace target header with 40pin edge-Connector
- add 17V converter (previously external)
- Screw-Connector now supports 7 - 17V
- remove XYZ - for this last version - testbed only
  - usb-input
  - harvester frontend
  - ~~external switch & LED~~
- pin-changes on BBB Sockets, documented in `shepherd-git/hardware/_deprecated/beaglebone_pinout_concept.xlsx`
  - P8_14 is GPIO7, was targets GPIO0
  - P8_17 is GPIO8, was targets GPIO1
  - P8_27 is pru1_GPIO8, was pru_uart_tx
  - P8_28 is pru1_GPIO10, in addition to PRU1-LED0 (switch to input)
  - P8_29 is pru1_GPIO9, was pru1_batOK (switch to input)
  - P8_30 is pru1_GPIO11, in addition to PRU1-LED1 (switch to input)
  - P8_37 is now controlling direction of gpio-group A
  - P8_38 is now controlling direction of gpio-group B
  - P8_40 is pru1_GPIO7, was pru_uart_rx
  - P9_14 is now controlling direction of gpio-group C, was EN_Recorder
  - P9_25 is free, was CS_ADC2_REC
  - P9_27 is PWR_GOOD_L, was CS_DAC_REC
  - P9_41B is PWR_GOOD_H, was CS_ADC1_REC
- Target mapping Changed!
  - Target-GPIO9..11 are now input pru0-r31 (P8_29, P8_28, P8_30)
  - Target_GPIO0 is now UART-RX
  - BBone Pins changed
  - PinDirections are different
  - new BBone to target mapping is in separate section below, it now supports recording 12 pins
- GPS-Sync-Header added

## Implemented Changes v2.5d

- BOM-Trouble
  - NLAS4684 / NLAS4684FCT1G not available at all
    - Analog Switch, Dual SPDT, 500 mOhm Rds, 300 mA continuous, 500 mA peak, <10 nA Leakage (1 nA for -55 to 25°C)
    - we still have **~200x NLAS4684MN**, so will switch to that for now (+ larger, safer package)
  - PI5A4158 / PI5A4158ZAEX currently not avail
    - Analog Switch, Dual SPDT, 800 mOhm Rds, ~40 nA Leakage, high speed ~150 MHz with < 40 pF
    - PI3USB102G: 4 Ohm, 5V5 max, 6 pF, **BUT** 200 nA leakage
    - PI5A23157: 10 Ohm, 6V max, 18 pF, **BUT** 50 - 1000 nA leakage
    - **PI5A4157 / 729-PI5A4157CEX: single channel version of same IC, but only larger SC70 package (2.2x2.4) available**
    - **729-PI5A4157ZUEX**: UDFN-Package, 1x1 mm, mouser totally hides out of life parts, is in stock
  - LP2989-3.3 not avail as VSSOP-8 / TSOP
    - switch to WSON?
    - **926-LP2989AIMM33NOPB**, same but double the price
  - 10k 0402 667-ERJ-2GEJ103X -> 603-RC0402FR-7W10KL
  - 5.1k 0402 667-ERJ-2RKF5101X -> 603-RC0402FR-075K1L

BOM-Additions:
- 60x 649-77313-802-46LF, header 2x23
- 10x 667-ERA-3ARW102V, 1k-0603-0.05%
- 10x 754-RG1608N-101-W-T1, 100R-0603-0.05%

Manual Mods (not final):

- xp: add 150R as LP for Emu-InAmp (~50kHz)
- xp: double C141, C3 (Emu around U32 Opa)
- xp: 10mV Ref input - C149 - 1uF + 10uF

TODO:
- software changes
- harvester seems a bit too fast - current is overswinging - see SM141K04LV ivcurve
- disable GPIO IO if voltage is cut (due to low_threshold)
- switch to usb PD with 12V?

## Errors of v2.5d

- button-connector has no paste on gnd-pads

## Pin Def

### Target Port - Cape 2.4

```
pru_reg     name            BB_pin	sys_pin sys_reg
r31_00      TARGET_GPIO0    P8_45	P8_14, g0[26] -> 26
r31_01      TARGET_GPIO1    P8_46	P8_17, g0[27] -> 27
r31_02      TARGET_GPIO2    P8_43	P8_16, g1[14] -> 46
r31_03      TARGET_GPIO3    P8_44	P8_15, g1[15] -> 47
r31_04      TARGET_GPIO4    P8_41	P8_26, g1[29] -> 61
r31_05      TARGET_GPIO5    P8_42	P8_36, g2[16] -> 80
r31_06      TARGET_GPIO6    P8_39	P8_34, g2[17] -> 81
r31_07      TARGET_UART_RX  P8_40	P9_26, g0[14] -> 14
r31_08      TARGET_UART_TX  P8_27	P9_24, g0[15] -> 15
r30_09/out  TARGET_BAT_OK   P8_29	-
```

### Target Port - Cape 2.5

```
pru_reg       name              BB_pin	sys_pin sys_reg
pru1_r31_00   TARGET_GPIO0/uRx  P8_45	P9_26, g0[14] -> 14 (also Sys/PRU-UART)
pru1_r31_01   TARGET_GPIO1/uTx  P8_46	P9_24, g0[15] -> 15 (also Sys/PRU-UART)
pru1_r31_02   TARGET_GPIO2      P8_43	P8_16, g1[14] -> 46
pru1_r31_03   TARGET_GPIO3      P8_44	P8_15, g1[15] -> 47
pru1_r31_04   TARGET_GPIO4      P8_41	P8_26, g1[29] -> 61
pru1_r31_05   TARGET_GPIO5      P8_42	P8_36, g2[16] -> 80
pru1_r31_06   TARGET_GPIO6      P8_39	P8_34, g2[17] -> 81
pru1_r31_07   TARGET_GPIO7      P8_40	P8_14, g0[26] -> 26
pru1_r31_08   TARGET_GPIO8      P8_27	P8_17, g0[27] -> 27
pru1_r31_09   TARGET_GPIO9      P8_29	-
pru1_r31_10   TARGET_GPIO10     P8_28   - !! PRU1-LED0, direction must be changed in DTree for debugging
pru1_r31_11   TARGET_GPIO11     P8_30   - !! PRU1-LED1, direction must be changed in DTree

pru0_r30_05   PWR_GOOD_L        P9_27     (was CS_DAC_REC), gets added to bit 12 for GPIO-Sampling
pru0_r30_06   PWR_GOOD_H        P9_41B    (was CS_ADC1_REC), gets added to bit 13 for GPIO-Sampling
pru0_r30_07   -                 P9_25     (was CS_ADC2_REC)
```

# solder paste

- loctite GC 10 only 100 g and more
- chip quik
  - SMDLTLFP 15 T4, 15g, Sn42/Bi57.6/Ag0.4
  - **TS391LT50**, 50g, T4 (20-38 microns), Sn42/Bi57.6/Ag0.4, Lead Free, No Clean, Thermally Stable, LOW TEMP 140°C
  - TS391SNL50, 50g, T4, Sn96.5/Ag03/Cu0.5, Lead Free, No Clean, Thermally Stable, 220°C
  - T4 (20-38 microns)
  - T5 (15-25 microns)
  - T6 (5-15)
  - SMDLTLFP10T5, 35g, T5, Sn42/Bi57.6/Ag0.4, Lead Free, Low Temperature
  - **SMD291SNL10T5**, 35g, T5 (15-25 microns), Sn96.5/Ag3.0/Cu0.5, Lead Free, 217-220C, refridge > 6 month, room > 2 month
  - good filters: https://www.chipquik.com/store/product_info.php?products_id=440012
- msp430FR-datasheet states compliance to jedec j-std-020 reflow profile
- ordered: 31 parts Target, SMD291SNL10T5, TS391LT50

# extra PCBs

- RP2350 - test - connector
- harvesting frontends
-

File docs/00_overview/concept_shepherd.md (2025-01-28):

# Concept for Shepherd V2

A more detailed moved to [shepherd/docs/dev/v2_improvements.rst](https://github.com/orgua/shepherd/blob/main/docs/dev/v2_improvements.md)

## Overview

- (mobile) testbed for battery-less IoT
- observer-nodes for an IoT-Target
- works autonomous or time-synchronized with a network backplane
- "software defined power source", emulation of
    - harvesting source (pre-recorded, simulated)
    - regulator / converter - circuit
    - intermediate storage-capacitor
    - "software defined" is largely true, but changing basic behavior needs a deep dive into PRU-Code
- allows to experiment with emulated spatio-temporal energy availability
- recording of energy-traces ⇾ key-parameters like current-drain and (virtual) capacitor-voltage
- additional functionality: recording of harvesting sources (not part of testbed)

## Nodes

- embedded linux board with shepherd-cape
- time critical code runs on two real-time processors
- two targets-ports are available
    - both can be supplied with individual voltages, only one is current-tracked
    - general purpose IO, target selection independent of power-supply-selection
    - separate 3V3 line
- bidirectional GPIO on 10 channels, 2x2 lanes are currently reserved for SWD / Spy-by-Wire, UART
- Targets (currently planned)
    - nRF52840
    - MSP430

## Testbed

- 30 Nodes on one floor in a university office-building
- nodes powered via POE
- (optional) one PTP-Masterclock, Node with GPS
- 1 Ubuntu Control-vServer, 10 TB of additional Storage
- 1 experiment at a time, no concurrency
- Web-Framework
    - user-management (roles for admins and users)
    - experiment-management, configure and control, add data (see below)
    - experiment-scheduling, calendar (set active, start-time, duration)
    - data management / quota (retrieve / delete recordings)
    - authentication via external services
    - E-Mail notifications
    - testbed status, topology
    - (optional) grafana visualization of recorded data
    - (admins) server status, quota, testbed control
    - documentation and instructions
    - target-management (specify slots of nodes)
    - (optional) benchmark-management (post-scripts)
- user-provided data (experiment management)
    - (optional) energy-traces, IV-Curves
    - regulator / converter-config
    - target-firmware
    - (optional) python userspace script that interacts with gpio / serial

## Technical details

- BeagleBone Green with 1 Core for Linux and heavy use of PRU for low-latency code
- target-voltage 0 to 4.5 V, max 50 mA per Target
    - 16 bit DAC, LSB results in 76 uV
    - 100 kHz sampling rate, jitter max +- 90 ns, 95% Quantile is 60 ns
    - 18 bit ADC, LSB results in 19.1 uV or 191 nA
- speed of voltage-drive
    - DAC has 0.75 V/us slew and 7 to 10 us settling (error < 0.x %)
    - OpAmp has 5 V/us slew
    - following Lowpass has corner-frequency of 16 kHz
    - 10 kHz on-off-patterns should be well in range
- low noise & high precision design for analog frontend
- 10 shared GPIOs with system
    - bidirectional level translation works from ~ 1.3 to 5 V
    - line is driven by PUs, always matched to target-voltage (low power usage)
    - recording: sampling rate is asynchronous, between ~ 1 to 5 MHz
    - data throughput untested, but edges look fine for > 1 MBaud
    - leakage during operation < 2 uA from target-side
    - gpio can be turned off, < 10 nA leak from target-side
- data-rates
    - 1 min ~ >= 54 MiB of measurement data (more with heavy GPIO actions)
    - 1 Hour, 30 Nodes ⇾ 100 GiB uncompressed (hdf5)
- time-synchronization
    - in linux via PTP,
    - chip-select edge of two test-nodes have a maximum jitter of about +- 300 ns, 95% quantile is 160 ns
- external watchdog for wakeup / restart on
- network
    - Server has 10 GBit Link to Switch
    - Nodes have 100 MBit Link to Switch

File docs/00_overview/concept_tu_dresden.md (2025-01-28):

# Concept for TU Dresden & ZIH

## Administrative Info

- ZIH offers hosting of (self provided) physical server and virtual ones
    - see ZIH Server-FAQ Link below
    - phyServer: gets power, ethernet, USV, cooling, ...
    - vServer: preferred by ZIH, free of charge, 3-5 Days prepare ⇾ vServer-SelfService link below
    - ZIH offers Sub-Domains on Website ⇾ SubDomain-FAQ link below
    - extended storage can be requested for research-groups: Gruppenlaufwerk link below
- ZIH-Rules for using their infrastructure
    - central dhcp: only by IT-Admin of facility ⇾ DHCP-FAQ link below
    - network access: IT-Admin [FAQ](https://tu-dresden.de/zih/dienste/service-katalog/arbeitsumgebung/bereitstellung_datennetz)
    - see cfaed IT-Admin link below
    - WIFI interference und network capability undocumented online
- Answer to inquiry, from IT / ZIH
    - we could use right side of nw-sockets (currently mostly unpatched) ⇾ TODO: talk with the leaders of groups that occupy offices
    - vLAN and DHCP from ZIH
    - we could use the server-room in BAR
    - ZIH offers more powerful vServers than listed on website
    - distribution plan shows that patch-cables of the floor all end in the same patch-room (BAR II65 S2/S3)
        - if switches do not meet our standards we can provide our own, needs to be a supported cisco model
        - if even that does not suffice it will get a lot harder ⇾ bringing new cable / devices into the wall is a structural change with a whole book of needed permissions
    - if LAN-Sockets do not suffice, we can use a (cisco-)switch locally in offices
    - unix-nodes should host fusion-inventory (to scan for vulnerabilities)
    - hardware > 150 € needs to be in inventory (sticker & database listing)
    - vServer gets monitored / managed with Centreon
        - for access from outside (internet) the server needs a security-concept
    - passwords and access-data should be managed with "TeamPass" ⇾ password manager for groups

**Link-Sammlung**:

- Server-FAQ: <https://tu-dresden.de/zih/dienste/service-katalog/zusammenarbeiten-und-forschen/server_hosting>
- DHCP-FAQ: <https://tu-dresden.de/zih/dienste/service-katalog/arbeitsumgebung/zentrale_ip_adressverwaltung>
- SubDomain-FAQ: <https://tu-dresden.de/zih/dienste/service-katalog/arbeitsumgebung/domains-dns/management>
- IT-Admin: <https://cfaed.tu-dresden.de/it-support>
- vServer-SelfService: <https://selfservice.zih.tu-dresden.de/l/index.php/cloud_dienste>
- Floor-plan: <https://navigator.tu-dresden.de/etplan/bar/02>
- Gruppenlaufwerk: <https://selfservice.zih.tu-dresden.de/l/index.php/spor/request-form/>

## RF-Measurement

- sender was a nRF52840-DK Board with BLE Beacon example, 1 MBit,
    - tx power - 16 to 8 dBm, in this case 0 and 8 dBm
    - rx sensitivity is - 97 dBm
- receiver was a phone, oneplus 3T, with visualization of rx-power,
    - rx sensitivity down to - 100 dBm
    - path loss in direct proximity was about 50 dB
- measurement-mode: determine max range while using link-budget and keeping stable connection
- results for 0 dBm
    - range was about 4 offices (horizontal) with dry-wall in between
    - was not able to get to upper floor
    - no signal through II800
- results for 8 dBm
    - range is about 7 offices (horizontal) with dry-wall in between
    - packets reached upper floor, even the adjacent office next to the direct overlying one
    - no signal through II800, not even with direct wall contact (these are massive walls, with massive metal / ventilation parts inside
- with active use of II64 / II64B / II64C it would be possible to get a U-Shaped network
- see "2020-12-15_rf_measurements.ods" for protocol

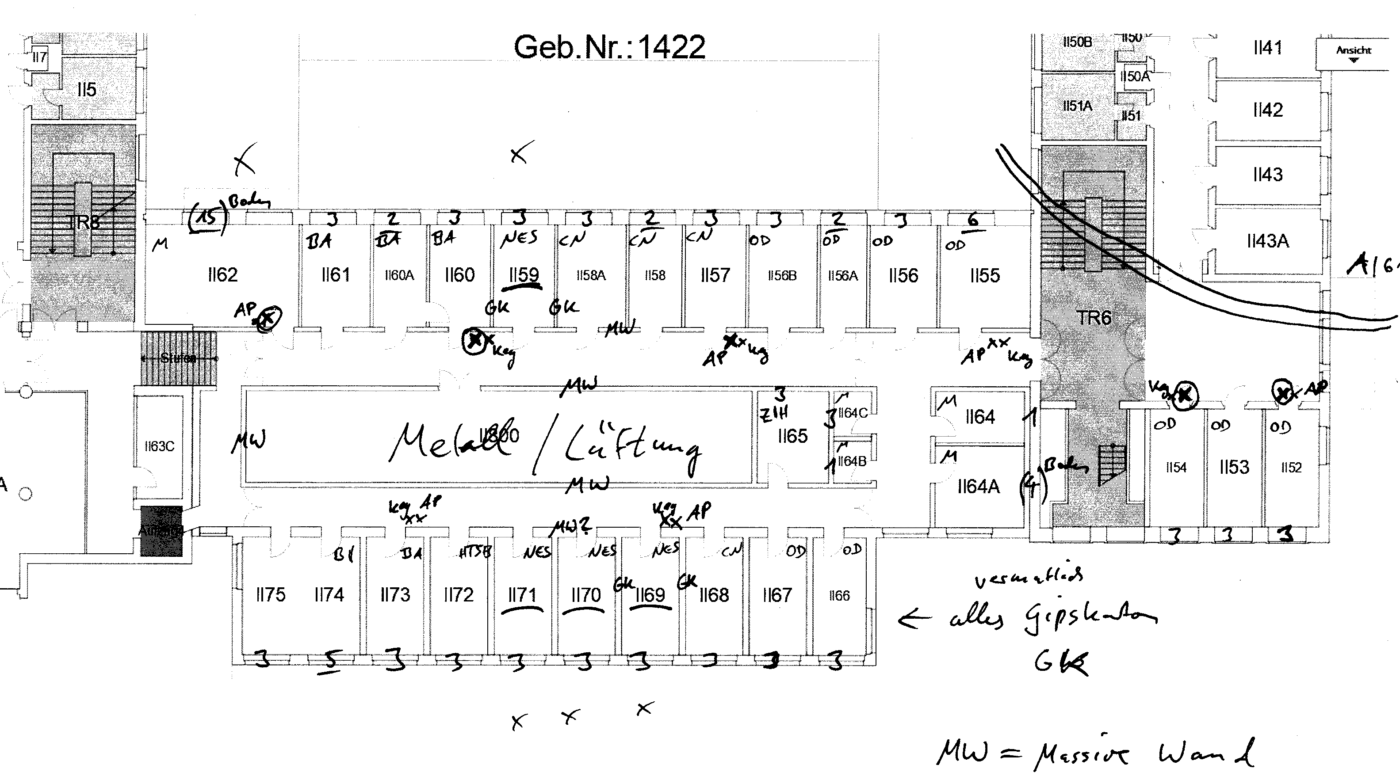
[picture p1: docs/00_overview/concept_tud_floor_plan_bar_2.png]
floor plan bar 2


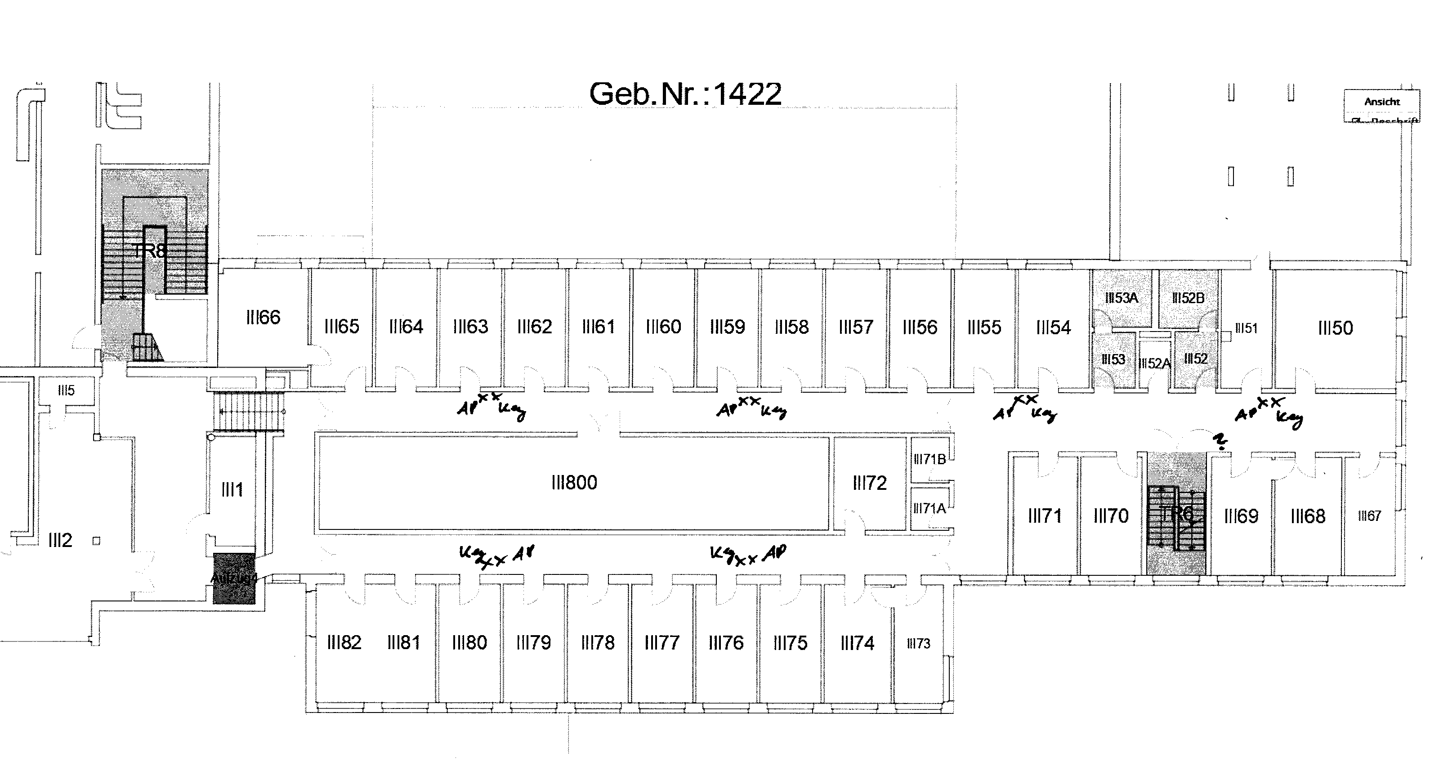
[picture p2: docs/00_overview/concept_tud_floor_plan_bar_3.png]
floor plan bar 3


## Netzkonzept für das ZIH

- Projektbeschreibung
    - Prüfstand für Funknetzwerk-Algorithmen, speziell im Bereich Energy-Harvesting
    - Nachbildung verschiedener Funktopologien und Energie-Szenarien
- Start des Projekts
    - 01.02.2021 (falls ein direktes Datum benötigt wird)
    - es läuft bereits, daher so bald wie möglich
- Projektlaufzeit
    - drei Doktoranden benötigen das Projekt für ihre Forschung für 3-5 Jahre
- Gerätetypen, Menge, Kategorien
    - ~ 30 autonome Funkknoten mit Netzwerk-Backchannel, Basis sind Beaglebone Green, Einplatinenrechner mit Linux / Debian-Derivat
    - die ersten 10 Testknoten sind bereits einsatzfähig
    - die Linux-Knoten haben ihr eigenes vLAN und wurden gegen Zugriff abgesichert (keine offenen Ports, kein UART, starke PW)
    - Kategorisierung am ehesten als Laborgerät?
- Einsatzort
    - Verteilung der Knoten auf der unteren cfaed-Etage im Barkhausen Bau
    - mehrere Räume, BAR II52 - II75
    - einige Knoten auf den Fluren, Kopierraum, Postraum, Konferenzraum
    - Problem: durch den großen Lüftungsraum II800 wird das Funknetzwerk sehr fragmentiert, sodass ein Nutzen oben angesprochenen Räume wünschenswert ist
- Schutzbedarf
    - Geräte zeichnen nur Energieverläufe der Funkknoten und deren GPIO-Traces auf
    - keine sonstigen Sensoren werden ausgewertet
    - keine Nutzerbezogenen Daten
- Dienste, Zugriff
    - Koten befinden sich in eigenem vLAN,
    - Knoten bauen SSH-Verbindung (Port 22) zum virtuellen ZIH Kontroll-Server auf um Roh-Messdaten zu übertragen
    - PTP (Port 319/320) zur Synchronisierung der Knoten untereinander, t_delta <= 100 ns
    - Internet-Zugriff für die Knoten wäre wünschenswert (für Updates, bzw. für die Einrichtung)
- Funknetzwerk des Prüfstandes
    - RF Netzwerk befindet sich im 2.4 GHz ISM-Band, bleibt innerhalb der ETSI-Norm, hauptsächlich IEEE 802.15.4, beispiel Bluetooth
    - Bluetooth belegt 81x 1 MHz breite Kanäle von 2400 - 2480 MHz und benutzt Frequency-Hopping, d.h jedes Paket wird auf einem anderen Kanal gesendet, mehrere tausend Sprünge pro Sekunde
- Besondere Anforderungen
    - Ethernet-Rückkanal der Knoten braucht Unterstützung für GBE, PoE, wenn möglich PTP nativ im Switch
    - im Bestfall wäre PoE abschaltbar (vom Kontrollserver) um das Netzwerk auszuschalten (Energiesparen), oder einzelne Knoten neuzustarten
    - PTP-Anforderung: Synchronisationsabweichung << 1 us zwischen den Knoten, optimal wären 10-100 ns
- wir sind offen für alle administrativen bzw. Sicherheits-Auflagen die notwendig sind zur Erfüllung der Anforderungen

## Gesprächsprotokoll mit dem ZIH-Treffen

- unsere Anforderungen wurden kommuniziert und angenommen, Punkte die mehr diskutiert wurden sind hier angeführt
- Cisco-Wifi-Router
    - das ZIH hat ein temporäres (sowie dauerhaftes) Abschalten von WLAN im 2.4 GHz Band auf der Etage angeboten
    - wir würden das Angebot gerne Annehmen, aktuell halten wir beispielsweise ein regelmäßiges Scheduling für Samstag / Sonntag ab sinnvollsten
    - betroffene sechs Router (+NW-Dose)
        - BAR-AP-A-II52 (II65_S2_K_21)
        - BAR-AP-A-II56 (II65_S2_K_13)
        - BAR-AP-A-II57 (II65_S2_J_7)
        - BAR-AP-A-II62 (II65_S2_H_13)
        - BAR-AP-A-II69 (II65_S3_B_15)
        - BAR-AP-A-II73 (II65_S3_C_17)
- zu beschaltene NW-Dosen
    - Laut Aussage vom ZIH dürften wir (mit niedrigster Priorität) ebenfalls NW-Dosen auf den Fluren bzw. öffentlich genutzen Räumen benutzen
    - siehe Liste unter <https://github.com/orgua/shepherd_v2_planning/blob/master/10_cfaed_ethernet_ports.ods>
    - Dosen bleiben weiterhin normal benutzbar, da vLAN per MAC-Filter funktioniert
- Kontrolle über POE
    - laut ZIH denkbar, wenn ein dedizierter Switch für den Prüfstand zum Einsatz kommt
- PTP-Zeitsynchronisation
    - laut ZIH optimal, wenn ein dedizierter Switch für den Prüfstand zum Einsatz käme
    - Jitter der Switches unter geringer Last angeblich sehr gering, im Datenblatt spezifiziert

## Entwicklung zur Infrastruktur (2021-01-29)

- Switch vom ZIH gestellt und gemanaged - WS-C2960X-48FPD-L
- 10 GBit Uplink zum Server, wenn Port frei ist (ist er)
- Nur NES-Lab-Netz auf den gewünschten Dosen
- Switch erlaubt POE mit insgesamt 740 W, also 40 Geräte a 15 Watt sind abgedeckt, BB brauchen ~3 W
- POE nicht dynamisch vom Server schaltbar, sondern nur händisch von IT
- PTP nicht nativ vom Switch unterstützt, aber der ist später austauschbar (Eigenleistung von uns)
- Dosen im öffentlichen Raum weiterhin generell ok, aber explizit untergeordnet und erst nach Begehung mit OK vom ZIH

- 10 TB Gruppenlaufwerk
    - self-service, funktionslogin
    - dom.ts.[].zih.... - account hinzufügen, admins volle Rechte, mehr Gruppenmitglieder hinzufügen
    - zugangsdaten im tu-passwortspeicher ablegen
    - einbinden über fstab als smb-lw, spezielle root-rechte
- Server Roadmap
    - mit fake ssl zum laufen bekommen
    - self service ⇾ sicherheits-prüfung kontinierlich durchgeführt
    - subdomain shepherd.cfaed. ... beantragen
    - ssl-zertifikat anfordern (anleitung ZIH) ⇾ kein pW-Schutz beim private Key, sonst ist bei jedem boot ein PW erforderlich
- Webseite
    - Barrierefreiheit und Impressum, sonst keine Weltweite freigabe (und ssl-force, subdomain)

## Anforderungen

- vLan
    - Zugriff vom Kontroll-Server aus, SSH (TCP Port 22)
    - Internet-Zugriff der Knoten für Linux-Updates
    - maximale Größe 45 Geräte
    - Campusgeroutet, ...
    - autorisierte MAC-Adressen landen automatisch im vLAN
    - TODO: MAC-Adress-Liste
- vServer als Kontroll- und Web-Interface
    - (die engen Zeitsynchronisierungsvorgaben gelten hier nicht)
    - Software die benötigt wird: Debian Linux Derivat, python 3.7+, ansible
    - >>100 GB scratch-area
    - Port 80 erreichbar aus dem Internet für Web-Interface, im Bestfall mit Sub-Domain oder eingebettet in CFAED-Seite
    - Personenbezogene Daten: später werden für die User-Accounts eventuell Email-Adressen gespeichert, eventuell umgehbar mit OAuth
- Cisco-Wifi-Router
    - das ZIH hat ein temporäres Abschalten von WLAN im 2.4 GHz Band angeboten
    - wir würden das Angebot gerne Annehmen, aktuell halten wir beispielsweise ein regelmäßiges Scheduling für Samstag / Sonntag ab sinnvollsten
    - betroffene sechs Router (+NW-Dose)
        - BAR-AP-A-II52 (II65_S2_K_21)
        - BAR-AP-A-II56 (II65_S2_K_13)
        - BAR-AP-A-II57 (II65_S2_J_7)
        - BAR-AP-A-II62 (II65_S2_H_13)
        - BAR-AP-A-II69 (II65_S3_B_15)
        - BAR-AP-A-II73 (II65_S3_C_17)
- zu beschaltene NW-Dosen
    - Laut Aussage vom ZIH dürften wir (mit niedrigster Priorität) ebenfalls NW-Dosen auf den Fluren benutzen
    - siehe Liste unter <https://github.com/orgua/shepherd_v2_planning/blob/master/10_cfaed_ethernet_ports.ods>
    - Dosen bleiben weiterhin normal benutzbar, da vLAN per MAC-Filter funktioniert
- NW-Switch in Raum II65
    - GBE (maximal benötigte Geschwindigkeit)
    - optimal ist ein dediziertes Gerät mit >= 40 Ports ⇾ Ziel: sehr geringer Jitter bei PTP-Zeitsynchronisierung der Knoten
    - vLan-Zugriff für Knoten
    - wenn möglich Kontrolle über POE der Ports zum Energiesparen, da embedded Knoten zwar runtergefahren werden können, aber kein WOL beherrschen

## Anbringung der Knoten

- controlled by: https://tu-dresden.de/tu-dresden/organisation/zentrale-universitaetsverwaltung/dezernat-4-gebaeudemanagement/sg-4-1-baumanagement/bautechnik
- formular:  https://www.verw.tu-dresden.de/VerwRicht/Formulare/download.asp?file=Baubedarfsblatt.pdf

- die Projektlaufzeit beträgt etwa 3-5 Jahre
- die 30 Testknoten benötigen als Verbindung lediglich jeweils ein LAN-Kabel
- Das Gehäuse kann entweder flach oder würfelförmig werden, das benötigte Volumen beträgt etwa 0.5 Liter
- Das enthaltene System verbraucht etwa 3-5 W bei Aktivität (5V), bedeutet also keine signifikante Wärmequelle
- wir beschränken uns auf die cfaed-Etage mit den Räumen BAR II52 - II75
- in der Auswahl sind hauptsächlich Büros, Kaffeeküche, Postraum, ein Konferenzraum und einige Flur-Positionen
- wir haben das OK von den Lehrstühlen, bzw. der Bürobesetzung und vom ZIH
- das ZIH hat bereits ein Subnetz für uns geschaltet

## Anforderungen zur Anbringung

- Genehmigung der Bundesnetzagentur (Funk)
    - wir operieren im ISM-Band und halten uns an die geltenen Bestimmungen, bzw. nutzen wir OEM / off-the-shelf-Funk-Module, zertifiziert
- Einzeichnung Standorte in Grundrisse
    - Standorte müssen noch ermitteln werden
- Zustimmung der aktuellen Nutzer ist schriftlich vom Kostenstellenverantwortlichen zu zeichnen
- Standorte im Flur und der Küche ⇾ separater Antrag an das Sachgebiet 4.3
- ggf. Brandschutzbewertung notwendig ⇾ Kostenstelle in Höhe ca. 1-1,5 TEuro benötigt
    - Formular von Herrn Heyner
- formloses Betreiberkonzept
- Gefährdungsbeurteilung ist mit der Arbeitssicherheit SG 4.5 abzustimmen

## Plan zur Anbringung

- Gehäuse
    - Elektronik nicht anfassbar, aber Belüftung möglich
    - keine leicht entflammbaren Materialien
- Betreiberkonzept Vorentwurf
- mit SG 4.3 in Verbindung setzen
- mit SG 4.5 in Verbindung setzen

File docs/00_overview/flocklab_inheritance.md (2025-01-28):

# Inheriting Flocklab

## The Package

- 30 complete observer-nodes (current deployment)
- one laptop as server
- and / or 25 boards as extension, replacement or second flocklab-testbed

## Current State

- flocklab is open-source, with no plans to commercialize
- testbed is very mature and stable (nodes only fail rarely, 1 node in 2y)
- most maintenance is for (new) users that break the interface or services (in a novel way)
- software is consisting of

    - observer: python 3.4 scripts, c programs, pru firmware (rocketlogger and one pru completely programmed in assembly)
    - server: python scripts, php web-frontend, mysql-database, xml-parsing
    - flocklab-tools: python-lib for uploading experiments, analyzing and visualizing data

- some things to be aware of

    - system is mature, but software is aging slowly for ~ 4 - 6 years
    - flock-beaglebone uses debian 9, kernel 4.14, python 3.4 ⇾ should be separated in a network with no internet-access
    - there are no unittests!
    - some things are destined to fail, ie. for experiments there is a 1 minute setup and finalizing phase, after that the next experiment can run. but with power traces enabled the data collection from the beaglebones creates high cpu-usage and may crash the followup experiment

- relocation overhead was seen as minimal - mostly changing the URLs and bringing the server online
- Stats (2022-6)

    - 35 active users, last 12 month
    - 5 minutes mean test duration
    - with covid the usage decreased but it is rising again
    - currently 15 % utilization
    - most used modules (from high to low): serial, gpio tracing, actuation, power profiling,
    - most used targets: dpp2-lora, nrf,

- wireless energy traces were planned for special nodes, also interference-generators

## Why should we inherit Flocklab

- do we learn something from running it?
- do we plan to use it more frequently?
- there are two other interested parties / maintainers

## Flocklab Details

API: https://gitlab.ethz.ch/tec/public/flocklab/wiki/-/wikis/Man/Services

XML: https://gitlab.ethz.ch/tec/public/flocklab/wiki/-/wikis/Man/XmlConfig#debug-configuration

- it is possible to configure a test online, download the xml and use variations of it for later experiments

- experiments

    - 1 minute setup and finalizing time ⇾ copy data, start services
	- copying (scp) continues and may collide with followup experiment

- a lot of code is in scripts - 2 cronjobs, 1 SQL-DB (setup-script for structure in git), PHP Frontend

- rarely to no defects for sd-cards or emmc-storage
- GPIO sampling

    - written as ASM-File / firmware, 20 Cycles, 10 Mhz, but only shortly with full bandwidth
    - there are two buffers that are read from userspace ⇾ ~ 16 kB
	- 10 MHz only for short period of time ⇾ after that only ~ 500 kHz

- no unittests, only manual testing

- cleaner - for stuck and zombie threads / experiments
- visualizierung ⇾ bokeh, web

- rocketlogger is pru-code + analog frontend (8 channel, 24 bit ADC)

- sync with gps is sub 100 ns accurate
- sync with ptp is only < 10 us ⇾ most definitely caused by nw-switch

- adc for current measurement can capture single digit nano-amps - but noise is reducing resolution to ~ 100 nA

## Learnings and Homework for Shepherd

- flocklab backbone / infrastructure is not helpful for shepherd, but the mature APIs collect years of user-experience
- interference and wireless energy traces would be awesome to have ⇾ simulated channel environment would be best ⇾ without that the tests are not reliably reproducible

- targets

    - tmote target is good for publicity (msp430 + cc2420) but currently only rarely used
    - uwb - is coming, low power and standardized,
    - Lora important ⇾ but power draw is ~ 150 mA, +22db, sx1262+ ⇾ but there are ICs with only 14 dBm

- 16 stations with years of solar traces, before and after solar cell
- lower sampling rates are useful for users (less data, faster processing & download)
- uart should be available as plain text with start- and end-timestamp (postprocessing on server)
- frontend

    - updates and maintenance messages per email
    - high level overview for data useful ⇾ plots with bokeh
    - flockid variable of the taget-images will be patched with node-id
    - sweep for automated tests very useful ⇾ also add human readable fields (title & description) to encode documentation
    - netcat link to beaglebones ⇾ serial-interface to targets
    - User can choose which observer ID (fixed hardware ID) is part of the experiment ⇾ gets (re)numbered as node ID (also used as flockid for target-fw)
    - some or most logs can be compiled to one per experiment (currently one per observer)

- backend

    - testbed should collect hardware-id / cpu serial of targets and map out what kind of target is where
    - better error-management ⇾ log everything
    - beaglebone-status is not necessarily part of the user-data
    - gpio actuation (!!!!) with level, offset, period, count
    - unused modules (power tracing, ...) can really be turned of ⇾ saves overhead
    - use checksums for firmware and traces ⇾ reusable with that ID

- managed userbase with quotas seems like a valid approach

- beaglebones ethernet interface can lock up ⇾ bbbrtc unlock, long reset ⇾ josh.com
- add plausibility tests, ie. BBone pings server and restarts if not accessible
- writing in bulk to RAM seems important - as the PRU locks up the ARM-Core
- PRU: min & max cycles per loop for both PRUs
- simulation is interesting ⇾ only solar ? iv-curve ⇾ basic idea: take an embedded system, remove solar cell and connect it to our testbed

- sub ms sync - xx us - for debug traces

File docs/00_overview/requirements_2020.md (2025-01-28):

# V2 Requirements (2020)

## Testbed-Infrastructure

- 12 - 30 nodes ⇾ depending on budget calculations
- distributed on one floor, several rooms
- use own infrastructure or parts of the university
- dedicated server or (better) use infrastructure of ZIH
   - contains: user data, web interface, shepherd controller
- WIFI + other RF-Standards as controllable interference
- support for channel monitoring, either packet- or spectral-based

## Test-procedure

- only 1 experiment, no concurrency
- reservation with calender-tool
- internal tests have higher priority

## Hardware - Cape & Capelets

- `>=2` Target-Ports with preselection before measurement (software defined targets)
    - nice to have: second target continues to get powered, so there would be a choice to support two different targets or one target and a monitoring device
- record traces for >= 4 Target-GPIOs (better 8 - 16), if 8 then 8+1 would be perfect
- Target-GPIO-Connection bidirectional, usable per script
- Target-UART-Connection support for several baud-rates, if possible >= 1MBit
- additional synchronous serial interface (i.e. SPI) for target
- mostly standardized data interfaces to all kind of targets
    - SDR-Target (with user programmable FPGA)
    - interferer
- reliable timebase (<=100ns deviation)
   - support for external sync-Line
- support for other Targets beside nRF52 (i.e. Long Range) and programmer (JTAG, SWD, ..)
- mobility of nodes (low prio), means two things moving system as well as distant long range nodes
    - req 1: tcp based (mobile network) for control-side-channel
    - req 2: scheduler via pre-configuration (node needs access to time-base)
- virtual capacitor and DC-Converter (real ones are either removed or bridged)
   - harvesting-traces remain basic input source
- support for On-Off-Pattern for power source (capacitor is currently interfering)
- Remote-Debugging not needed
- recording of harvesting traces not part of big testbeds → saves some money for parts
- variable TX-Power for multi-hop-scenario
- simple and fast to modify casing is ok

## Software - Script-Support / API

- support user-contributed energy-traces for targets, also offer preselected default ones
- support individual energy-traces per node
- control GPIOs (copy, for reference)
- dynamic addressing of targets (firmware-manipulation before flashing)
- API modular and encapsulated ⇾ separation between scenario and measurement, for reusability
- allow switching between targets

## Software - Website / Frontend

- user-management, permission / role management
- Quota
- authentication via external service like OAuth (i.e. Github)
- Upload: Scripts, Harvesting-Traces, Firmware
- Scratch-Area for user-data
- integrated tests for measurement: test for plausibility, pre-run in software (abstract virtual hardware)
- scheduler for measurement, time to prepare and follow up (data transfer, conversion, compression, ...)
- manipulation of target-firmware to individualize ID and TX-Power
- results downloadable by user, for a certain time
- feedback via e-mail - measurement start, data available, error, shortly before deletion
- grafana-visualization
- documentation and instructions

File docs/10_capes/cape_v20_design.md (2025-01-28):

# Cape v2.0 - PCB Changes

## General rule for assembly-drawings

- origin orientation
    - keepout
    - assembly notes (mech15)
- designator
    - keepout
    - top designator (mech 2?)
- Copper / Silk
    - L1 Pads / Via
    - Keepout
    - Top Overlay
⇾ print in Color

## Implemented Changes v2.0r0

- 4 Layer! Planes for Sig, GND, A5V, (3V3)
- decide Manufacturer, EC, Aisler, Betalayout
- add design rules
- add layer stackup
- add default vias
- divide in groups / rooms
- optimize surroundings of ICs
- change vias of pson50, dfn-10 (by lt3487 spec)
- move lvlchangers to the left
- change pads of pinheaders in inner layers
- thermal pad of switch unused? yes, no word of use in datasheet
- increase restring / holesize, sheph seems to have 0.15mm holes?, target 0.075 ring

## Implemented Changes v2.0r1

- Beaglebone
- Emulator
    - DAC
        - previous: **DAC8562SDGSR**, mouser 595-DAC8562SDGSR
            - 50 MHz SPI, 7-10 us Settling, 1-4 mV Zero-Scale-Error, 40 mA Short-Circuit-Current,
        - constraints: >= 16 bit, SMD, 2 CH, not maxim, v-range ~2.5...5.5 V, short settling time
            - this could also be low-res and slow for only bq-output-sim, but it would benefit to also tap in cap-voltage directly
            - https://www.mouser.de/Semiconductors/Data-Converter-ICs/Digital-to-Analog-Converters-DAC/_/N-4c44d?P=1z0w8k6Z1z0w2wwZ1z0w2wvZ1z0w2wtZ1z0z7ptZ1yz5pwlZ1yzmm10Z1yzml2aZ1yzmm18Z1yzmlprZ1yzmm0yZ1yzmm13Z1yzmlr9Z1yzmlh1Z1yzmlwtZ1yzmm16Z1yzmm0zZ1yyh4l4Z1z0zls6Z1yzxao2&Ns=Pricing%7c0
        - replacement: AD5663ARMZ-REEL7, mouser 584-AD5663ARMZ-R7
            - 50 MHz SPI, 4 us Settling, Zero-Scale-Error<1mV, 30mA Shor-Circuit-Current, needs voltage reference, WATCH OUT - there are versions with midpoint-start
        - replacement: DAC8830, 1-CH, 50 MHz, 16bit, 10nV/sqrtHz, 1us Settling,
        - replacement: AD5545B, 2-CH, 50
    - OpAmp for V-BUF 2CH?
        - previous: **OPA2388IDGKT**, digikey 296-50277-2-ND
            - 30-60 mA perm, 5 V/us, 7 nV / sqrtHz, 0.25 uV Offset,
        - constraints: opAmp, 3CH, supply ~ 3-5 V, Rail2Rail
            - https://www.mouser.de/Semiconductors/Integrated-Circuits-ICs/Amplifier-ICs/Operational-Amplifiers-Op-Amps/_/N-6j73m?P=1yzxao0Z1yzmm18Z1yzmm0xZ1yzmm13Z1yzmm14&Ns=Pricing|0
        - replacement: AD8606ARMZ-REEL, mouser 584-AD8606ARMZ-R
            - 2CH, 80 mA, 5 V/us, 8 nV/sqrtHz, 20 uV Input Offset,
    - shunt-Resistor
        - nRF52 takes 9 mA @ 4dBm, 16 mA @ 8 dBm for ~ 200 us, rest is below 2 mA,
        - previous: 2 Ohm 1% ⇾ 16 mA => 32 mV, would mean 1% Voltage drop at 3V3, less would be better
        - current sensors are no alternative, too expensive, not enough resolution
        - replacement: 1 Ohm 0.1% ⇾ 1:1 mA:mA, 0603 or 1206
            - **RT1206BRD071RL**, mouser 603-RT1206BRD071RL
    - OP-Amp for Shunt
        - previous: AD8422BRMZ in combination with LM27762DSSR
        - constraints: 1 CH, > 2 MHz Gain-BW-Product, Supply ~ 2-5 V, >75 dB CMRR, Low input offset voltage
        - replacement: **INA331AIDGKR**, mouser 595-INA331AIDGKR, in combination with **LM7705** (-0.23V) on V-, mouser 926-LM7705MMX/NOPB
            - ref: https://e2e.ti.com/support/amplifiers/f/14/t/700003
        - proper replacement: ad8429B
            - https://tools.analog.com/en/diamond/#difL=0&difR=0.05&difSl=0&gain=100&l=0&pr=AD8429&r=5&sl=0&tab=1&ty=2&vn=-8&vp=9&vr=0
            - https://training.ti.com/system/files/docs/1312%20-%20Noise%202%20-%20slides.pdf
    - ADC 2CH
        - previous: ADS8694TSSOP38 4 CH
            - 18 bit, 4 CH, two V-Rails for A&D, 500 kSPS, 18 MHz SPI, variable LPF, 1175 ns Acq & 825 ns Conv.
        - constraints: 2CH, 18-24 Bit, SMD, >100 kSPS
        - replacement: **ADS8691**, 1CH 1 MSPS 8€, ADS8695 1CH 500kSPS 9€, ADS8699 1CH 100kSPS 6€, Acq 335/1000/5000ns, Conv 665/1000/5000ns
    - analog switch ⇾ is there a way to power the offline target? Switch up supplies
        - previous: TMUX1101DCK, 4 Ohm, 1 SPST SinglePole-SingleThrow
        - constraints: 2 Ch, legs, supply >= 5, rdson <= 500 mOhm,
        - replacement: **NLAS4684MR2G**, mouser 863-NLAS4684MR2G, 2CH, 300 mA Conti, 500 mOhm rds
    - Target-Port-IO (GPIO, SPI, I2C, UART, SWD/JTAG, BAT_OK PRU) ⇾ Q: is HS-GPIO enough? rest is userspace-logged
- debug to target
    - voltage-level-translator,
        - previous1: TXB0304RUTR BiDir, autosense, min 3mA input drive current, 4 CH, >40 Mbps
        - previous2: SN74LV4T125PWR UniDir
        - constraints: 1 Mbps, high channelcount, autosensing, 2-5V, HighZ-Mode
        - replacement: **NXS0108PWJ**, mouser 771-NXS0108PWJ, 50 Mbps, BiDir, Autosense, open drain, 8 Bit, NXB-Version: 2mA input drive req.
            - ⇾ WARNING: expected 18.01.2021, **nxs0101** already in stock, nxs0102 in may
- target-port ⇾ default pin-header, maybe smaller version of it
- suppply for second target ⇾ 2. CH of DAC + Buffer
- status-Leds
    - green 575nm, 0603, 60mcd 2V@20mA, 150060VS55040, mouser 710-150060VS55040
    - blue 470nm, 0603, 80 mcd 3.2V@60mA, 150060BS55040, mouser 710-150060BS55040
    - red 645nm, 0603, 70 mcd, 2V@20mA, 150060SS55040, mouser 710-150060SS55040
    - orange 605nm, 0603, 100 mcd, 2.2V@20mA,
- LEDs for current active (and powered) Target
- multipurpose nChannel MosFet
    - constraints: <50mOhm, smd, n-CHannel, VGS <=700mV
    - sot-323-3: DMN2058UW-7, mouser 621-DMN2058UW-7
- i2c-storage, prev: CAT24C256WI-GT3
- Cage
- Part Properties:
    - price (for ten), manufacturer, manufacturer id, shop 1, shop 1 ID, ...
    - special properties: max voltage, power, current, size / package, color, forward Voltage
- extra information (i2c-adress, spi-speed, ) directly in schematic
- power-recording-stage
    - DAC DAC80501ZDGSR
    - OPAmp OPA388ID, pin-compatible with LTC2050HV
    - nMOS SI2374DS, test with BSH103
    - ShuntOPAmp Ina190A1IDCKR
- power in via vdd_5v (P5/6) ⇾ Test shows: BB does not power up via sys_5v
- reboot / boot via Pin-Toggle (Shutdown via command), we should trigger both (RESn⇾PD,PWR⇾PD), Test shows: Reset works while PWR is in PD
- add 256 GB USB-Stick
- switch to smaller IC-Packages and 0402
- order / add GPS
- is the gps capable of alarm (wake up sys)
- our 5V analog should be stabilized more! Add A5V with 2 Stage Bead, or real coil
- add footprint for layer-windows
- add footprint for shepherd-logo
- give INA190 a negative supply (>1mV would be enough) on GND-pin, ref stays on common gnd, extra decouple
- Debug-Pins with Ground
- extend harvest-Port, add option to measure VSense, and output VCap (V_A of Emulator)
- it would be wise to detach a5v even further from 5V, with a low-drop diode
- EMI-guard SPI, currentlimit at pinheader, terminate at ICs, 33 Ohms close to cpu recommended (avoid reflections)
- add alarm-feature, something SPI-programmable, that can act like a watchdog, with at least max 1-4h windows
- check against shepherd v1.5
- don't shut down individual Emu / Rec - Parts (delete or just disable all at once) ⇾ done by Pwr-control
- Harvester needs second channel ADC with very low input current, 1MOhm is too low
- manual button with LED ⇾ connector S4B-ZR-SM4A-TF, P1 3V3, P2 LED ODrain, P3 SenseButton with PU, P4-6 GND
- add ultra low noise LDO to A5V, and possibly a boost-converter upfront
- find better level translator, less current (best if near 0)
- reprocessed 11_concept.file
- switched Ina190 for AD8421
- added boost/Inverter for proper voltage rail
- add target port (comparator-include?) System will be a nRF52840 and most likely a MSP430
    - try to make it compatible with breadboard / dev-Kit
    - is spy-by-wire physically compatible with swd ⇾ it is, TClock is uni-dir, TDIO is bi-dir
- replace 100nF/16, 1uF/16, 10uF/16
- BOM, more precise alternative - BB uses 32.768 kHz osci MC-306 (20 ppm, 8x3.8mm) or similar, package says 327A5M
    - alternative: 5 ppm, 12.5pF, 50 kOhm, https://www.mouser.de/ProductDetail/Citizen-FineDevice/CM200C32768HZFT?qs=rkhjVJ6%2F3ELrGt3qchcVtQ%3D%3D
    - BB also uses 24.576 MHz
- check output limits of opax388 and DAC
- compare lowNoise LDO to LM27762
- 750 kOhm 1%,  667-ERJ-2RKF7503X, 5 + 32
- connect BB-Pins, 500 Ohm to input pins that could be driven from both sides
- complete ERC
- 1uF/16V is still 0603, change to 0402, there are 34x (incl. Recorder)
- redistribute capacitors
- replace coil with smaller one, check recommended direction
- add 1kR & 100R high precision for current measurement, EMU
- order digikey (extBut, samtec), mouser, csv
- add footprint for quality-control-panel
- BB Pinheader Cape-Design Stays ⇾ possible alternaltive Producer is Samtech, design is now divided
- add production-constraints
- update BOM
- v2r1 ordered

## Implemented Changes v2.0r2

- silkscreen - 10k array are 1k
- 3d-Step: shield transparent for better view below
- silk. "P3" designator is below component
- pads of 0402 bigger, 1.2x1.2 as min area for pads? paste 0.8x0.8? got some tombstones on current revision
   - half a pad distance to neighbour (keepout)
- improve connection betwenn pads (esp. 0402)
- feducial seems massive, shrink it?
- SPI-CS with at least 33R to lower chance of interference
- R for BatteryGood is wrong (handled by PRU), should it also be routed to userspace?
- TC7WH-Footprint is to large
- HC2G-comment (Name) is wrong / twisted
- DAC pads could be longer, reach more under the IC
- MP32 has no dot on package, just [ABC], lower left is pin1
- NSR (or all diodes) could get a line on the 3d-file (current dot is confusing, because the actual package has line and dot)
- the orange led is red! ... bad UI for general blinking
- describe gain of OP-Amp in schematic
- 100R, accuracy is missing in description / constraints
- Silk for L9/L10
- essential silk-numbers on headers can be bigger/bold, a bit more distance from header
- rename rec to harvest, port on pcb more obvious
- harvest dAC ch-b - drain power source OK?
- improve marking on Voltages, maybe with an arrow
- reverse diode of mosfet is too weak - already destroyed the reverse polarity protection
- some popular Flag-Markers on backside for pinheader
- Pin1 dot should be a shallow/sharp triangle, pointing in the right direction (less confusing in dense layouts)
- transistor-footprint is not conform to datasheet, it is slighly bigger and just misses the pads?!?
- u13 thermal to wide, reduce a bit to avoid shorts (u15 has same possible weakness)
- rework als Pin-Descriptions (already mentioned)
- round and divided (big) paste pads
- add general power-led when shepherd is on? maybe on 6V line
- switch to thinner stencil, bigger pads (paste is good for it)
- header-row on target has paste, it should not
- Font/Writing in copper is unreadable on target (slighly below spec)
- add layer for manual / pick'and'place descriptions (m15, m?)
- qr code is not readable, blurred, reduce size of "pixel"
- warning for harvest V_sense ⇾ Voltage floats if not connected and will most likely show V-Max in this state
- ADC nRST should not get A5V, only 3.3, also there is no need for a resistor-switch
- Connector for external switch was copied from old schematic, but this one had inversed pin-numbering on connector, different from datasheet
- Testpoint on RVS-Pin of
- protect GND better around Pinheaders
- U25A, Inputs are switched
- diode between both 5V-lines should be two diodes that feed the watchdog
- 3V3 should also be switched - maybe even the 5V0 in, so the PU that hinder bootup are meaningless
- vias came back only weak tainted (make it less severe if that happens), mainly for target pcb
- more distance to gnd-plane (soldering is hard, even with thermals
- TEST Watchdog, make compatible with BB
- TEST GPIO to and from target
- same orientation for transistors
- switch p8-27 and 29 (batOK / GPIO4) for cleaner readout
- switch p8-43/44 with p8-39/40 for proper boot
- TEST boot with all pins except 3v3 & 5V
- but make sure that shepherd-EN (p8-13) stays low during boot
- switching main power to both targets shows, that the routes seem to have different current-readings for the same load! odd
- 1k for LEDs
- check surroundings of mosfets, size has changed
- mosfet of watchdog-wake could be tied to 3V3 with additional 1k resistor or diode (so that button stays usable)
    - 100k PD for wd-pin (or keep 10k)
    - 3V3 goes low on powerdown, so watchdog can enable (pull low wake) BB again,
    - polling has no effect during normal operation
    - TEST if 1k is enough to pull line low to enable ⇾ it is
- add open source hardware logo?

## Schematic Changes - Open

- prepare calibration
- ordered not enough 15uH Coils, need 30 more
- check remainder of BOM for emu-only assembly
- shepV1 had a user-space led, which is still there, same pin, but pru-controlled, was it the same in v1?
- explain schematics,

## Part Changes

Note: after Mouser-Order - NOW already ordered

- DAC       100nF ⇾ 1uF
- Boost     10uF ⇾ 10uF (inv)
- Inv       +47uF
- Rec       2x 10k 0603 ⇾ 0402
- All       34x 1uF/16V/0603 ⇾ 1uF/25V/0402
- final Shield, cover & frame
- all       4x 15uH/4mm ⇾ 15uH/3mm
- parts of nRF-Target

## Schematic Changes Postponed

- internal calibration? with 2 switches and 1 calibration-linear-power-supply
- OP-Amp, bias Subtractor: LMP7701MF, not needed now
- sync to pps ⇾ external pcb
- usb-socket is impossible to hand-solder right now
- (maybe) add PU to watchdog outputs
- separate PCBs for PPS-Source, Recorder, Emulator

### Open Issues

- only 5 diodes of type PMEG in order?
- change 100 uF to 47u? one less component
- Testpad should be square for GND, half-circle for Signal or similar
- r3 (dac, emu)
- proper naming for TP if there is space

- TPs should have bigger hole, so probes stick
- oscillating opAmp should be outside of cage
- allow install of a big cap on A5V or 5V, 5v5 1F is cheap
- add longer pinheader for p8/p9 23-46

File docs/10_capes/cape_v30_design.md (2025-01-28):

# Cape v3.0 - PCB Changes (WIP)

## Main-Changes

- switch from Beaglebone to Raspberry Compute Module (CM4 for now)
- design modular sub-PCBs
- allow 4 Targets

## TODO NextGen

- change ADC to higher resolution?
  - better: stabilize reading, lower noise level
- use second input of ADC to monitor actual voltage?
- make system modular !!
  - (+) less complexity -> dedicated emu OR hrv
  - (-) cal-data is harder to store, sync
  - (+) hrv can be ported to other platforms (cheaper, scalable)
  - (+) changing subsystems is easier
- direction pin GPO:3 for leveltranslators is named strangely
- rename Recorder ⇾ Harvester
- switch to rpi Cm4 Platform !!!
- offer gps-port with pps & uart on Cape
- put single gpio-lines onto SWD-IO switches (switch 2x for free)? or is dir controlled by PRU?
  - Switchable Directions:
  - Group A = GPIO 0:3 -> Group C GPIO2:5
  - Group B = GPIO 8 -> Group A GPIO0
  - Group C = GPIO 9 -> Group B GPIO1
- Sensor for light intensity on harv node?
- try to drive 150 - 200 mA to Target
  - change OP-Ampdriver to higher current output? Double Opa388?
- try to offer more than 10 GPIO to target (Goal=16)
- all GPIO should at least be INPUTs, some (2-4) also switchable

## Modularization

- would allow specialized observers (Hrv OR Emu)
- Cape mostly does routing between modules (and target-Ports)
- sub-PCBs are reusable (and changeable)
- harvesting with a cheaper network of nrf52 + pwr + hrv (rf-syncronized)
- a generalized USB-Interface + Hubs would allow usage on all (usb-capable) hosts

### Host-Interface / Header

- 2x4+ pins for MCU-Links
- 1 pin clock-sync-input
- 1 pin enable shepherd
- 1 pin reset host (predefined)
- 10..16 pins gpio-tracing (optional, mirrored)
- 2 pins for dir selection (optional, mirrored)
- 4 pins for programming (optional, mirrored)
- 2x USB to MCUs
=> 10 pins min, 26..32 pins optionally in total

### PWR-Module

Header

- GND
- 3 inputs (Enable, 5V, <= 17V)
- 4 Output (L3V3, -6V, L5V, 10V)
  - 10mV becomes part of Emu
- enable-signal (could also be on main PCB)

### EMU / HRV Module

Content

- MCU (maybe RP2040)
- DACs & ADCs, Current-Shunt

Header

- GND
- 4 voltages in (L3V3, L5V, 10V, -6V)
- **Variation A - MCU on Module**
  - 4 pins for host-link (i.e. SPI)
  - 1 pin Clock-Sync Input
  - 2 pin Output as Power-good-signal (or sync-channels for target)
  - Note: it might be more advantageous to keep the MCU off this module
- Variation B - 'dumb' standalone module
  - 6 pins to analog frontend (3 SPI, 3 SPI-CS)
  - 1 pin reset / enable (optional)
  - ~~(generalized) - no enable needed~~
- 4 voltages outputs (2 Rails, 2 Feedback)

GPIO-Budget

- 4+ pins for host-link
  - SPI? must manage 100 kHz * 2 * 32 bit = 6.4 MBit/s
  - due to FPU this could be 2x18 (raw) in both directions
- 6 pins to analog frontend (3x SPI + 3x CS)
- 1..2 pins for target selection (set once, 2 or 4 Ports)
- 1 pin reset
=> 12..13+ pins in total

Voltage-Rating of Current-Sensing-Input of Harvester

- R & C -> 50 V
- OPA189 -> supply 36 V max (+10/-6 V for us), input (v+)+0.5V
  - NOTE: opamp only drives between 0..5 V and it will pull down the sensing-input-line
- AD8421 -> max -Vs + 40 V = 34 V

### GPIO-Trace-Module

Content

- MCU (maybe RP2040)
- levelshifter
- Current limiting resistors
- voltage buffer?

GPIO-Budget

- 4+ pins for Host-Link (SPI, or similar)
- 1 pin Clock-Sync Input
- 10..16 pins gpio-tracing
- 2..4 pins for direction selection
- 2 pins for logging power good (optional?)
=> 19..27+ pins in total

Programmer GPIO-Budget

- 4+ pins for Host-Link OR just USB
- 4 pins for programming (SWD, SBW, JTAG)
- 2 pins for direction selection
- todo: add boot-pin to enable automatic remote flashing?
- todo: always add debug-connector (swd + gnd)
=> 10 pins in total

## 4-Way Switching

- allows more targets

### Current 2-Way solution

NLAS4684 (for voltage-routing)
- dual SPDT Analog Switch
- 500 mOhm RDS
- 300 mA continuous, 500 mA peak
- < 10 nA leak (~1 nA for -55..25°C) -> important
- 300 pF additional capacitance on line
  - datasheet shows 330 pF (ON) and 104 pF (OFF), typical
  - rise-time with 1kOhm shows 434 pF trace-capacity (with ~40pF from actual traces)
- 1V8..5V5

-> replacement: 4 Way, >= 5.5 V, <<10 nA leak, <= 500 mOhm RDS, >= 250 mA continuous

PI5A4158ZA (for gpio-routing)
- dual SPDT analog switch
- high bandwidth, 150 MHz,
- 500 mOhm (less relevant)
- < 40 pF added capacitance
- +-40 nA leakage
- strange package
- 1V65..5v5

-> replacement: 4 Way, >= 5.5 V, high bandwidth >40pF,

### replacements

- for more target-ports (=4)
- TODO: look through old notes, update PI-Altium data

## RPi + RP2040

Pi-40Pin-Header
- 28 GPIO, 2 SPI, 1 UART, SDIO

Pi4
- 1 GBE
- 28 GPIO, 5 SPI, 5 UART,
- CM4 has no usable USB, but raw PCIe 2x1 !
- runs stable, has enough power, cool to the touch

Pi5
- PCIe on extra connector, 5 GT/s
- requires 5.1V, 27 W
- pretty hot (~60°C) without sink
- RP1 handles most IO - not well documented ATM
  - triggering sync-gpio from kernel-module is harder (TBD)

- RP2040
  - pin 50..56 seems to have quad SPI (separate from GPIO)
  - USB2.0 Controller, Full Speed 12 Mbps
  - 30 GPIO

```ad-todo
- determine max SPI-Speed (rpi4-to-rp2040)
- determine max usb-throughput (rpi4-to-rp2040)
- do a demo pcb
- pcb for adapting new target
- firmware-update-options for RP2040
- rp2040 needs a big FIFO, option: program MCU directly and use large QSPI-Flash for
  - FRAM SPI Flash
  - but also RAM via SPI,
- pio example available - 48 MHZ, 8 bit wide, 380 Mbit
  - pio - fifo - dma - ram
- option for interface RPI - RP2040
  - direct SPI
  - ~~usb1.1 Full-Speed~~
  - RPI - usb3 - usb3-hub - ftdi QSPI - rp2040
  - parallel interface
  - cypress - usb2 480 MBit - free programmable - i.e. massstorage -
    - https://www.infineon.com/cms/en/product/universal-serial-bus/usb-peripheral-controllers-for-superspeed/ez-usb-fx3-usb-5gbps-peripheral-controller/
    - cyusb301### costs 20€/IC
    - usb-analyzer: https://www.ellisys.com/products/usbcompare.php
  - sdio
- Test:
  - RP2040 - serial usb firmware - max output - receive per terminal -
    - rpi should ask interface regularly, buffer on rp2040 should not overflow
    -
- SDIO is documented in https://datasheets.raspberrypi.com/rp1/rp1-peripherals.pdf, Chapter 4, Page 60
```

### Power-Output to Target

- req: 200 mA

### Improve Noise-Performance

- what did the uCurrent do?
- https://github.com/joeltroughton/uSMU
- jule counter of tegBed -> can we offer millivolt range with enhanced res?

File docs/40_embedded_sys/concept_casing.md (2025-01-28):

# Hardware Casing for Nodes (2020)

**Deprecated / shelved!** Current lasercut case is in [main repo](https://github.com/orgua/shepherd/tree/dev/hardware/case_lasercut)

## Constraints

- nodes can vanish, wander
    - fixate
    - keep inconspicuous (under desk an option?), make it look official / blend in
- nodes can spook new people in the same office
    - must look professional, official
    - be transparent about the function (inform current people in office, but also use sticker to provide a FAQ-Website
- must support cooling (direct sunlight, proximity to radiator)
    - convectional cooling would be the easiest
- must contain
    - BBone with shepherd Cape (75 x 55 x 25 mm)
    - POE-Converter (81 x 55 x 25 mm)
    - Target nodes (20 x 30 x 4 mm) - orthogonal on capelet or in direction of longest edge of capelet)
    - < 20 cm Network cable
    - power-connection
    - USB-Stick (45 x 20 x 9 mm)
    - opening for one RJ-45-Socket
- must be transparent to RF
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

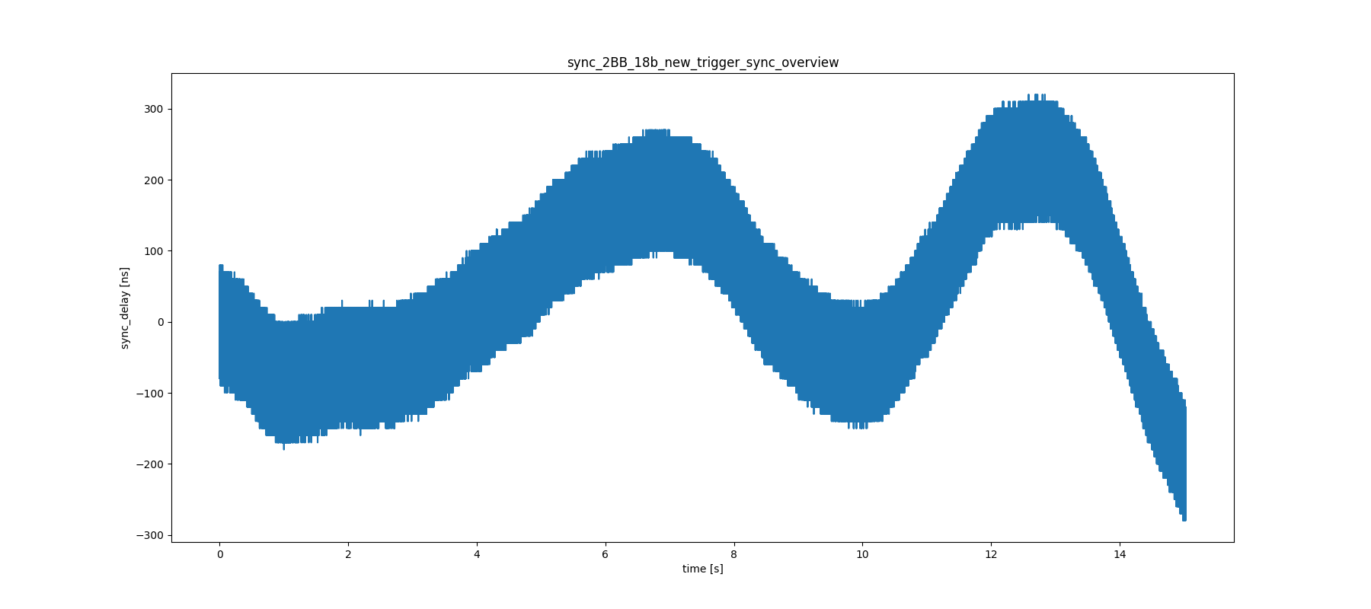
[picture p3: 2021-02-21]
docs/70_network/timesync_gpio_level_pru/sync_2BB_18b_new_trigger_sync_overview.png

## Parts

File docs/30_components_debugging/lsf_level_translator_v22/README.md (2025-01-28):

# LSFxyz GPIO Level Translators

**TLDR**: LSF-IC is not suited for the testbed - use translators with switchable direction

## Problem

- cape versions: v2.0 to v2.2 (and higher?)
- voltages on B-side seemed to work fine from 2.5 V to 5V, but showed errors below,
- Nexperia LSF0108 seems to have hidden properties that are not mentioned in the datasheet
- expected behavior
    - open drain on both sides when pins float / only PUs active
    - PUs bring pins to ref-voltage
    - a low on side results in a low on the opposite side

## Setup

- Side A has constant supply voltage of 3.3 V
- side B supply is dynamic, 0 to 5 V, but voltages below 1 V are not expected to be covered by the translator

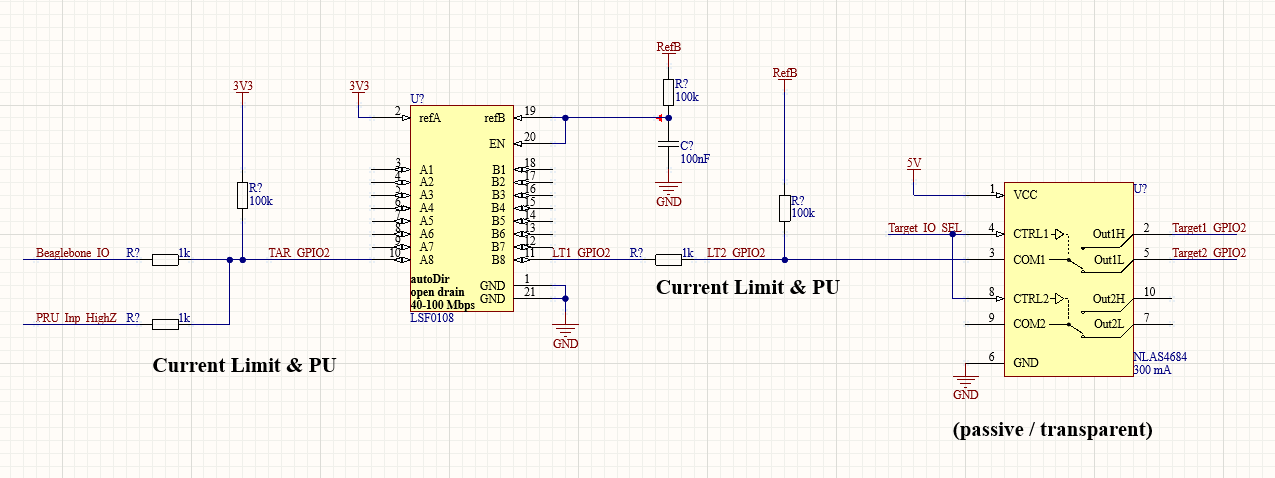
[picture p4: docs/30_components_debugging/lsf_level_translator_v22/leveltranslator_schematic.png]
lvl


## Nexperia LSF0108

- marketed as bidirectional, multivoltage, open-drain, push-pull
- translation between "0.95 V and 1.8, 2.5, 3.3 and 5V" (room for speculation)
- unlike the TI-Versions, this IC does not have voltage constraints (like V_A has to be >= 0.8 V + V_B)
- "An and Bn pins may be exchanged" (mentioned more than once)

## Measurements

- Low to high
    - V_RefA = 3v3, V_RefB = 4v5
    - both sides highZ, only PUs working ⇾ V_A and V_B settle at 1.2 V ⇾ UNEXPECTED, should be VRef
    - Side A tied to GND ⇾ V_B = 0 V
    - Side A tied to 3v3 ⇾ V_B = 3v3 ⇾ UNEXPECTED, V_B is capped at 3v3
    - Side B tied to GND ⇾ V_A = 0
    - Side B tied to 4V5 ⇾ V_A = 3 V
- High to Low
    - V_RefA = 3v3, V_RefB = 2v0
    - both sides highZ, only PUs working ⇾ V_A and V_B settle at 0.9 V ⇾ UNEXPECTED, should be VRef
    - Side A tied to GND ⇾ V_B = 0 V
    - Side A tied to 2v0 ⇾ V_B = 1v9 ⇾ UNEXPECTED, but ok
    - Side A tied to 3v3 ⇾ V_B = 2v0
    - Side B tied to GND ⇾ V_A = 0 V
    - Side B tied to 2V0 ⇾ V_A = 1.4 V ⇾ UNEXPECTED, still below detection threshold

## Fixing the LSF

- most answers are implied by: https://training.ti.com/multi-voltage-translation-lsf-family
- Bias Voltage
    - V_B (B for Bias?) needs 200 kOhm PU and V_B > V_A + 0.8 (TI-Rules don't hurt)
    - current will flow from B to A, limited by the 200 kOhm
    - voltage between RefA-to-B will be threshold voltage of FETs (V_B = V_Bias = V_A + V_thres)
    - video 8 in the series even shows a single VB supply schematic with a voltage divider on A-Side ⇾ see below
- V_A should be the lowest voltage in System, so V_A gets 1V from an additional supply
- PUs
    - PUs are possible on neither, one, both sides
    - not needed on sides that only drive (push-pull)
    - not needed on receiving low side with input leakage lower 1 uA
    - needed when level is not on corresponding level V_A or driver is only open drain
- both Ref-Voltages are independent of real voltages used on each side
- PUs on target side should not be driven by current-sensed line

**Single Supply Calculation (Maxima)**

```
# available parts, R1/R2 are part of a voltage divider on RefA-Side, R1 is the high side, R3 is current limiter of RefB:
R1: 1e6;
R2: 100e3;
R3: 240e3;
# VFet-Nexperia is 1 V, TI is 0.85 V (referring to datasheet), nexperia shows ~ 575 mV voltage drop
VFet: 0.575;
VB: 3.3;

R2 = R3 * R1 * VRefA / ((R3 + R1)*(VB - VRefA) - VFet * R1);
solve(R2, VRefA);

VRefAA: ((R2*R3 + R1*R2) * VB - R1 * R2 * VFet) / (R1*R2 + R1*R3 + R2*R3);
# VRefA = 0.89 V for TI, 0.85 V for Nexperia
```

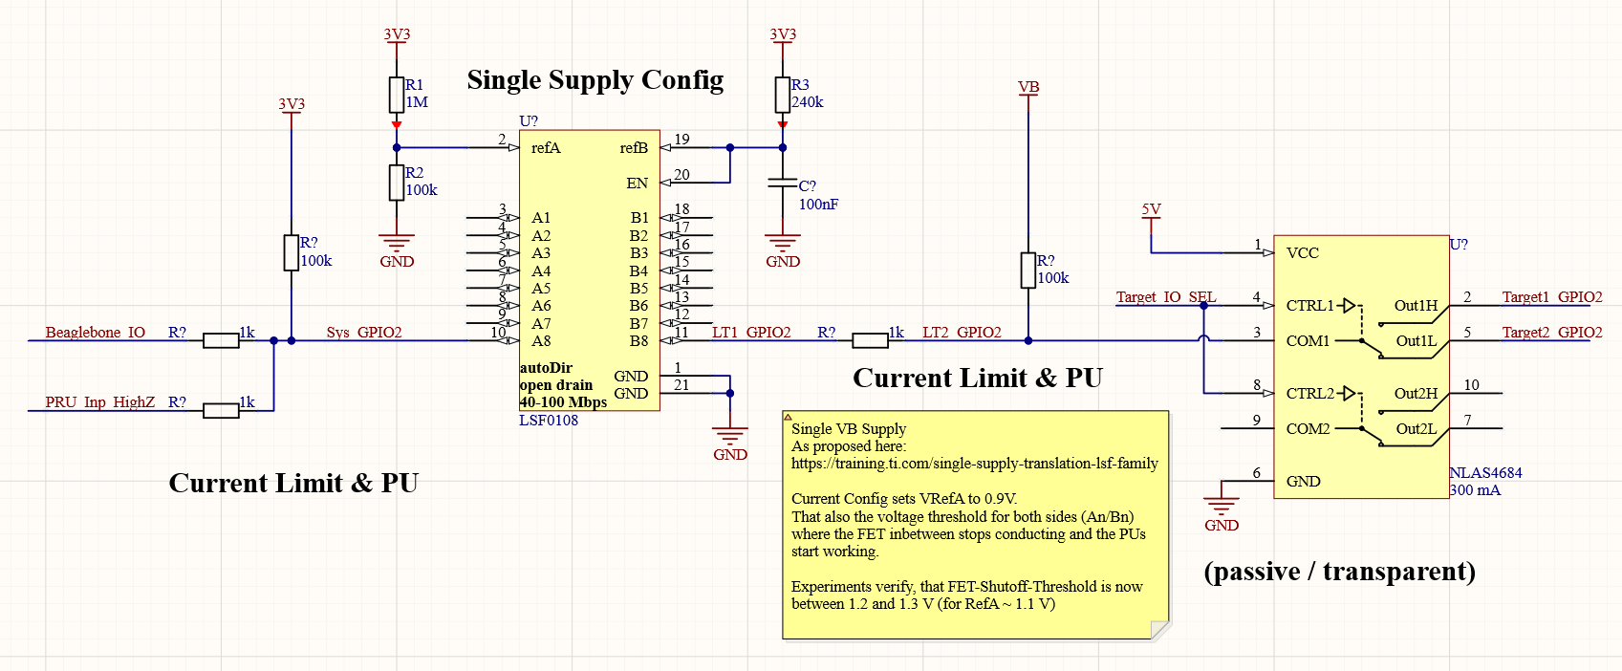
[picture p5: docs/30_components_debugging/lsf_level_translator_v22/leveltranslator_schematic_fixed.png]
lvl_fixed


## Single Supply Verification

- schematic above was recreated
- Ref A settles at 1.079 V, Ref B at 1.673 V ⇾ fet-diode seems to drop ~ 600 mV
- as soon as one side is above ~ 1.2 V (only tested 0.1 V steps), the other voltage is controlled by PU on that side
- Source-Meter on B-Side shows about 1 MOhm for High Signal (with PU of same voltage) down to ~ 1.2 V (< 0.4 uA)
- below threshold voltage
    - below 1.2 V the source meter controls the voltage on both channels (Pulldown)
    - from -8.3 uA at 1.1 V the sink-current grows to -45 uA at 0.0V (almost linear)
    - Side-A PU is 100k to 3.3 V  and Side-B PU is 100k to 1.3 V, results in
        - 33 + 13 uA to GND ⇾ matches closely with source-meter reading
        - 22 + 2 uA to 1.1 V ⇾ seems to flow into largely in B-Side-PU, because SM-Reading is lower
- without B-Side-PU
    - on B-Side the source meter supplied the following currents into B-Side
    - 1.5 uA @ 1.2 V (800 kOhm)
    - 5.3 uA @ 1.5 V (283 kOhm)
    - 9.2 uA @ 2.0 V (217 kOhm)
    - 13 uA @ 2.5 V (192 kOhm)
    - 17 uA @ 3.0 V (176 kOhm)
    - 21 uA @ 3.5 V (167 kOhm)
    - 25 uA @ 4.0 V (160 kOhm)
    - 29 uA @ 4.5 V (155 kOhm)
    - 32 uA @ 5.0 V (156 kOhm)

## Inner Workings

- CMOS Driver (Push-Pull) on one side, CMOS Receiver (High-Z) on other side, with PU on each side
- Driver LOW ⇾ current will sink into transmitter, current is generated by both PUs, FET / Translator will generate a small voltage drop
- Driver HIGH ⇾ FET / Translator will turn off (cut line) reaching VA, transmit-line is controlled by driver, receiver side by PU from then on

## Alternatives

- constraints: BiDir, Auto-sensing, one side 3v3, other side 1.7 - 5 V (nRF52)
    - TXB ⇾ needs relatively high driving current
    - TXS ⇾ has internal PU, but relies on VRef-Relation
    - LSF ⇾ only conducts on lowside, needs external PU
    - ICs from TI seem to always need special VRef-Relation
    - Nexperia ICs are new and on order (but offer better specs)
- special uniDir solutions
    - spi, sn74lv4t125, spi, https://www.ti.com/product/SN74LV4T125#product-details##features
    - 1bit unidir, sn74lv1t34, https://www.ti.com/product/SN74LV1T34#product-details##features
- voltage constraints could be solved by a two-stage approach 3v3 <⇾ 0v9 <-> 1.x - 5V
- BiDir with Dir-Pin
	- https://www.ti.com/lit/ds/symlink/sn74lvc2t45.pdf?ts=1625563250176&ref_url=https%253A%252F%252Fwww.ti.com%252Fproduct%252FSN74LVC2T45

## TODO

- previous: post-shunt-voltage was fed to level translators (PUs showed up in current-draw of target)
- currently pre-shunt-voltage is fed to level-translators
- cleaner solution
    - buffer post-shunt-voltage, saves one switch, but costs additional OPAs

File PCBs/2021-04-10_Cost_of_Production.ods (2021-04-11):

Shop | Item | net price / € | Quantity | Result
Eurocircuits | PCB Shepherd Cape v2.0r0 with Stencil | 51,67 | 3 | 155,00
Eurocircuits | PCB Shepherd Cape v2.0r1 with Stencil | 14,06 | 32 | 450,00
Eurocircuits | PCB Shepherd Cape v2.1 with Stencil | 14,38 | 32 | 460,00
Eurocircuits | PCB nRF-Target v2.0 with Stencil | 4,84 | 32 | 155,00
Eurocircuits | PCB nRF-Target v2.1 with Stencil | 5,47 | 32 | 175,00
 |  |  |  | 0,00
Mouser | Parts for Shepherd-Cape without Recorder | 68,96 | 32 | 2206,72
Mouser | Parts for Shepherd-Cape ONLY Recorder | 42,11 | 3 | 126,33
Mouser | Parts for nRF-Target | 13,18 | 33 | 434,94
Digikey | Parts for Shepherd-Cape (Pinheaders) | 5,58 | 32 | 178,42
 |  |  |  | 0,00
Betalayout | Solder Paste | 23,00 | 1 | 23,00
 | SMD-Assembly (Estimate) | 46,88 | 30 | 1406,25
 |  |  |  | 0,00
Formulor | Casing (Estimate) | 15,00 | 30 | 450,00
 |  |  |  | 0,00
CSV | USB-Sticks 128 GB (div brands) for testing | 16,67 | 3 | 50,00
ComputerUniverse | USB-Stick 256 GB, Philips FM25FD75B/00 | 25,90 | 30 | 777,00
CSV | POE-Adapter Kit for testing (TP-Link) | 21,00 | 1 | 21,00
alternate | POE-Splitter (TP-POE10R) | 11,00 | 30 | 330,00
rs-online | Bbone Green | 47,00 | 30 | 1410,00
ComputerUniverse | SD-Cards for flashing (PNY Pro Elite 32 GB) | 10,74 | 5 | 53,70
alternate | LAN-Cables 10-20cm (BB to POE) | 2,40 | 30 | 72,00
rs-online | LAN-Cables 50 - 300cm (POE to Wall) | 3,35 | 30 | 100,50
?kai? | Bbone AI for evaluation | 110,00 | 2 | 220,00
 |  |  |  | 0,00
 | Cisco Switch | 5907,00 | 0 | 0,00
 |  |  | SUM: | 9.254,86 €
ColorCoding
Blue Items | needed during dev
Orange Items | Estimate - not ordered yet

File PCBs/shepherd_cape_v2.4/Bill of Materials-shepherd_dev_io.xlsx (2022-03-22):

Comment | Description | Designator | Footprint | LibRef | Quantity | Manufacturer PN | Manufacturer | Distributer | Distributer PN | Price n10 [€]
C_0402_1uF_25V | Capacitor | C1, C2 | CAPC1005X06 | .C_0402_1uF_25V | 2 | GRM155R61E105KA12J | Murata | Mouser | 81-GRM155R61E105KA2J | 0.06
C_0402_100nF_25V | Capacitor | C3, C4, C5, C6, C7, C8 | CAPC1005X06 | .C_0402_100nF_25V | 6 | GRM155R71E104KE14J | Murata | Mouser | 81-GRM155R71E104KE4J | 0.025
HDR_2x9_2.54mm_socket | Gold, Straight | P1 | P_Pinheader_2x9_R2.54mm_female_angled | .P_HDR_2x9_2.54mm_female | 1 | SSQ-109-02-S-D-RA | Samtech | Mouser | 200-SSQ10902SDRA | 4,24
P_HDR_2x2_2.54mm_header | Gold, Straight, 5.80 mm Mating, 3.46 mm termination | P2, P3 | P_Pinheader_2x2_R2.54mm | .P_HDR_2x2_2.54mm_male | 2 | 861400042YO2319LF | Amphenol | Mouser | 649-86140042YO2319LF | 0.12
R_0402_470R | Resistor | R1, R3, R5, R7, R11, R12 | RESC1005X04 | .R_0402_470R_1% | 6 | ERJ-2RKF4700X | Panasonic | Mouser | 667-ERJ-2RKF4700X | 0.028
R_0402_100k_1% | Resistor | R2, R4, R6, R8, R15 | RESC1005X04 | .R_0402_100k | 5 | ERJ-2RKF1003X | Panasonic | Mouser | 667-ERJ-2RKF1003X | 0.02
R_0402_10k | Resistor | R9, R10, R16, R17 | RESC1005X04 | .R_0402_10k | 4 | ERJ-2GEJ103X | Panasonic | Mouser | 667-ERJ-2GEJ103X | 0.02
R_0402_1M | Resistor | R13 | RESC1005X04 | .R_0402_1M | 1 | ERJ-2GEJ105X | Panasonic | Mouser | 667-ERJ-2GEJ105X | 0.02
R_0402_240k_1% | Resistor 100ppm/C | R14 | RESC1005X04 | .R_0402_240k_1% | 1 | ERJ-2RKF2403X | Panasonic | Mouser | 667-ERJ-2RKF2403X | 0.02
R_0402_33R | Resistor | R18 | RESC1005X04 | .R_0402_33R | 1 | ERJ-2GEJ330X | Panasonic | Mouser | 667-ERJ-2GEJ330X | 0.02
R_0402_1k | Resistor | R19 | RESC1005X04 | .R_0402_1k | 1 | ERJ-2GEJ102X | Panasonic | Mouser | 667-ERJ-2GEJ102X | 0.02
U_DG612EEN | Quad single-pole single-throw analog switch, rail-to-rail, <<2nA low leakage, 3-7 pF low capacitance, single or dual supply | U1 | QFN40P180X260X60_HS-17N | DG612EEN | 1 | DG612EEN-T1-GE4 | Vishay | Mouser | 78-DG612EEN-T1-GE4 | 1.31
74LVC2T45GS | Dual supply translating transceiver; 3-state +-24 mA DriveCurrent 60 Mbps (1.5V) to 420 Mbps (>3V) | U2, U3 | SON35P100X35-8N | 74LVC2T45GS | 2 | 74LVC2T45GS,115 | Nexperia | Mouser | 771-74LVC2T45GS115 | 0.34
U_PI5A4158ZA | Analog Switch, Dual SPDT, 500 mOhm Rds, 300 mA continuous, 500 mA peak, <10 nA Leakage (1 nA for -55 to 25°C) Note: this IC is for PWR-Switching - it adds a capacitance > 300pA to the line | U4, U8 | SON50P100X80_HS-13N | PI5A4158ZA | 2 | PI5A4158ZAEX | Diodes Inc | Mouser | 729-PI5A4158ZAEX | 0.36
U_DG2501DB | Quad single-pole single-throw analog switch, rail-to-rail, <<1nA low leakage, 3-8 pF low capacitance, single or dual supply | U5 | BGA16C35P4X4_144X144X51 | DG2501DB | 1 | DG2501DB-T2-GE1 | Vishay | Mouser | 78-DG2501DB-T2-GE1 | 1.37
U_NLAS4684 | Analog Switch, Dual SPDT, 500 mOhm Rds, 300 mA continuous, 500 mA peak, <10 nA Leakage (1 nA for -55 to 25°C) | U6 | BGA12C50P4X3_196X146X65 | NLAS4684-FC | 1 | NLAS4684FCT1G | ON Semi | Mouser | 863-NLAS4684FCT1G | 0.80
U_LSF0108 | Level Translator, 8CH, auto direction sensing, open drain, VCCA 1.2-3.6V, VCCB 1.65-5.5V, 40-110 Mbps, 1-5uA leakage | U7 | QFN50P250X450X100_HS-21N | LSF0108 | 1 | LSF0108BQX | Nexperia | Mouser | 771-LSF0108BQX | 0.59
U_74HC4066 | Quad single-pole single-throw analog switch, CMOS | U9 | PQFN50P250X300X100_HS-15N | 74HC4066BQ | 1 | 74HC4066BQ,115 | Nexperia | Mouser | 771-HC4066BQ115 | 0.27

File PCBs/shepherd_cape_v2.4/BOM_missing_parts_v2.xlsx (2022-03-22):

Distributer | Manufacturer | Name | Manufacturer PN | Price [€] | Distributer PN | Quantity
Mouser - kai | Sensirion | Feuchtigkeitssensoren für Plattenmontage Humidity and Temperature Sensor | SHTC3 | 2.19 € | 403-SHTC3 | 10
Mouser - kai | Kyocera AVX | Schottky Dioden & Gleichrichter 40V 0.5A SIZE 0805 | SD0805S040S0R5 | 0.31 € | 581-SD0805S040S0R5 | 50
Mouser - kai | Vesper | MEMS-Mikrofone Wake-on-Sound Piezoeletric MEMS Mic Single-ended Analog I/F with ZPL | VM1010 | 1.45 € | 208-VM1010 | 10
Mouser - kai | Analog Devices Inc. | Analoge Komparatoren Nanopwr(300nA)COMPARATOR.w/2% Volt Ref | LTC1540CS8#PBF | 4.00 € | 584-LTC1540CS8#PBF | 15
Mouser - kai | E-Switch | Sensorschalter 50mA 12VDC SPST, NO 5mm Act, 160gf | TL3305BF160QG | 0.19 € | 612-TL3305BF160QG | 25
Mouser - kai | FCI / Amphenol | Sockel & Kabelgehäuse ECONOSTIK HEADER SR RA TH 1X20 | 10129379-920002BLF | 0.32 € | 649-1012937992002BLF | 20
Mouser | GCT | USB-Buchse | USB4125-GF-A | 0.43 | 640-USB4125-GF-A | 35
Mouser | Panasonic | R 5.1k | ERJ-2RKF5102X | 0.02 | 667-ERJ-2RKF5102X | 100
Mouser | TI | OPV | OPA189IDBVR | 2.02 | 595-OPA189IDBVR | 70
Mouser | Murata | C 100nF | GRM155R71E104KE14J | 0.02 | 81-GRM155R71E104KE4J | 1750
Mouser | Murata | C 10nF | GCM155R71E103KA37D | 0.02 | 81-GCM155R71E103KA7D | 350
Mouser | Panasonic | 33R | ERJ-2GEJ330X | 0.02 | 667-ERJ-2GEJ330X | 700
Mouser | Murata | C 1nF | GRM1555C1H102JA01D | 0.02 | 81-GRM1555C1H102JA1D | 560
~~Mouser~~ | ~~Panasonic~~ | ~~100R~~ | ~~ERJ-2GEJ101X~~ | ~~0.02~~ | ~~667-ERJ-2GEJ101X~~ | ~~0~~
Mouser | Panasonic | R 680k | ERJ-2RKF6803X | 0.02 | 667-ERJ-2RKF6803X | 100
Mouser | Murata | C 1uF | GCM155C71A105KE38D | 0.05 | 81-GCM155C71A105KE8D | 1540
~~Mouser~~ | ~~Nichicon~~ | ~~C 1mF~~ | ~~UVR0J102MPD1TD~~ | ~~0.25~~ | ~~647-UVR0J102MPD1TD~~ | 0
Mouser | Amphenol FCI | HDR 2x9 | 10129381-918001BLF | 0.28 | 649-1012938191801BLF | 40
Mouser | Panasonic | 2R | ERJ-2GEJ2R0X | 0.02 | 667-ERJ-2GEJ2R0X | 100
Mouser | Taiyo Yuden | C 100uF | JMK316ABJ107ML-T | 0.25 | 963-JMK316ABJ107ML-T | 200
Mouser | Yageo | 100R Ersatz | RC0402FR-7D100RL | 0.015 | 603-RC0402FR-7D100RL | 100
Mouser | Würth | C 470uF 25V | 860020474014 | 0.25 | 710-860020474014 | 50
Mouser | Würth | C 680uF 10V | 860020274013 | 0.2 | 710-860020274013 | 70

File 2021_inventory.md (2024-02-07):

## Inventory

- ~20 PoE Adapters (100 MBit)
- 10 - 15 Beaglebone Black / green, same amount of Shepherd V1.x Capes
- ZyXEL Ethernet Switch GS1900-24HP, with PoE
- Linksys Router WRT54GL
- uBlox Neo M8T

## Order List

TODO

- GPS-Module with external Antenna, uBlox LEA-M8F or ZED-F9T
- final GBE PoE Adapter, 20 €
    - <https://geizhals.de/?cat=switchgi&xf=12885_PoE-Splitter>
    - Possible Copy of POE-Splitter RPi-Hat <https://www.raspberrypi.org/forums/viewtopic.php?t=266617>
- Shepherd Cape, 15 €
- Shepherd Parts
- Target Capelet
- Target Parts
- Casing
- NAS or Server
    - ~ 250 € per 10 TB
    - 300 € for 4 Bay NAS, 800 € for 8 Bays
    - <https://geizhals.de/?cat=hdxnas&xf=12970_8%7E2659_ohne>
- [48 Port Managed Cisco NW Switch]

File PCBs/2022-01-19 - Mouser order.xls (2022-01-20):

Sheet: Sheet1
Comment | Manufacturer | Manufacturer PN | Distributer PN | Price [€] | Quantity
74LVC2T45GM | Nexperia | 74LVC2T45GM,125 | 771-74LVC2T45GM125 | 0.406 | 100
100 R | Panasonic | ERJ-2GEJ101X (https://www.mouser.de/ProductDetail/Panasonic/ERJ-2GEJ101X?qs=Cz%252B5TvT4ylzvFLU04D2DFQ%3D%3D) | 667-ERJ-2GEJ101X | 0.02 | 50
430 R | Panasonic | ERJ-2GEJ431X (https://www.mouser.de/ProductDetail/Panasonic/ERJ-2GEJ431X?qs=YMBIwoNQYdWkvumG%2FWRq4g%3D%3D) | 667-ERJ-2GEJ431X | 0.02 | 50
1 k | Panasonic | ERJ-2GEJ102X | 667-ERJ-2GEJ102X | 0.02 | 50
2 k | Yageo | AC0402JR-072KL (https://www.mouser.de/ProductDetail/YAGEO/AC0402JR-072KL?qs=ygRr%2Ftkhtet40d8iOckJVQ%3D%3D) | 603-AC0402JR-072KL | 0.02 | 50
2.7 k | Yageo | AC0402FR-072K7L (https://www.mouser.de/ProductDetail/YAGEO/AC0402FR-072K7L?qs=yhV1fb9g%2FKY0mUoSgfHwLw%3D%3D) | 603-AC0402FR-072K7L | 0.02 | 50
100 k | Yageo | AF0402FR-07100KL (https://www.mouser.de/ProductDetail/YAGEO/AF0402FR-07100KL?qs=HEu%2FF%2FCqxzIuS6oTgJlL0A%3D%3D) | 603-AF0402FR-07100KL | 0.03 | 50
1 M | Panasonic | ERJ-2GEJ105X (https://www.mouser.de/ProductDetail/Panasonic/ERJ-2GEJ105X?qs=H7k1u0Mp9JQDA6YNNR2WyQ%3D%3D) | 667-ERJ-2GEJ105X | 0.02 | 50
3.3 M | Panasonic | ERJ-2GEJ335X (https://www.mouser.de/ProductDetail/Panasonic/ERJ-2GEJ335X?qs=MVjVSMjNRMqJ%2FrpuVtP9Pg%3D%3D) | 667-ERJ-2GEJ335X | 0.02 | 50
10 M | Panasonic | ERJ-2GEJ106X (https://www.mouser.de/ProductDetail/Panasonic/ERJ-2GEJ106X?qs=6%252BUraArZVSBCZmk3hNWmDQ%3D%3D) | 667-ERJ-2GEJ106X | 0.02 | 50
1 nF | Murata | GRM1555C1H102JA01D | 81-GRM1555C1H102JA1D | 0.02 | 50
10 nF | Murata | GCM155R71E103KA37D | 81-GCM155R71E103KA7D | 0.02 | 50
100 nF | Taiyo Yuden | EMF105B7104MVHF | 963-EMF105B7104MVHF | 0.03 | 100
1 uF 25V | Murata | GRM155R61E105KA12J | 81-GRM155R61E105KA2J | 0.06 | 100
4.7 uF 6V3 | Murata | GRM155R60J475ME87D (https://www.mouser.de/ProductDetail/Murata-Electronics/GRM155R60J475ME87D?qs=pTGEtN%252BMLlBnU9jM8bPB0Q%3D%3D) | 81-GRM155R60J475ME8D | 0.05 | 50
10 uF 4V0 | Murata | GRM155R60G106ME01D (https://www.mouser.de/ProductDetail/Murata-Electronics/GRM155R60G106ME01D?qs=d0WKAl%252BL4KYRfB4EgQksjw%3D%3D) | 81-GRM155R60G106ME1D | 0.09 | 50
alternative | TI | OPA2388IDGKT | 595-OPA2388IDGKT | 3.43 | 40
alternative | Nexperia | 74HC2G04GW-Q100H | 771-74HC2G04GW-Q100H | 0.37 | 40
alternative | TI | OPA388IDBVT | 595-OPA388IDBVT | 2.52 | 40
alternative | TI | TPL5010DDCR | 595-TPL5010DDCT | 0.98 | 40
alternative | TI | OPA189IDBVT | 595-OPA189IDBVT | 2.47 | 40

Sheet: Sheet2
Distributer PN | Quantity
771-74LVC2T45GM125 | 100
667-ERJ-2GEJ101X | 50
667-ERJ-2GEJ431X | 50
667-ERJ-2GEJ102X | 50
603-AC0402JR-072KL | 50
603-AC0402FR-072K7L | 50
603-AF0402FR-07100KL | 50
667-ERJ-2GEJ105X | 50
667-ERJ-2GEJ335X | 50
667-ERJ-2GEJ106X | 50
81-GRM1555C1H102JA1D | 50
81-GCM155R71E103KA7D | 50
963-EMF105B7104MVHF | 100
81-GRM155R61E105KA2J | 100
81-GRM155R60J475ME8D | 50
81-GRM155R60G106ME1D | 50
595-OPA2388IDGKT | 40
771-74HC2G04GW-Q100H | 40
595-OPA388IDBVT | 40
595-TPL5010DDCT | 40
595-OPA189IDBVT | 40

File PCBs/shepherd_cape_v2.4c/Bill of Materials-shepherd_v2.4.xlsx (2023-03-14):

Comment | Designator | Footprint | LibRef | Quantity | Manufacturer | Manufacturer PN | Distributer | Distributer PN | Price n10 [€]
C_0402_1nF_50V | C1, C3, C28, C29, C34, C36, C73, C133, C141, C143, C147 | CAPC1005X06 | .C_0402_1nF_50V | 11 | Murata | GRM1555C1H102JA01D | Mouser | 81-GRM1555C1H102JA1D | 0.02
C_0402_100nF_25V | C2, C4, C11, C12, C14, C20, C22, C27, C30, C37, C43, C46, C52, C54, C56, C58, C60, C63, C66, C67, C70, C71, C74, C78, C79, C80, C84, C85, C86, C91, C98, C105, C108, C113, C118, C120, C122, C123, C124, C125, C126, C127, C128, C129, C136, C144, C155, C156 | CAPC1005X06 | .C_0402_100nF_25V | 48 | Murata | GRM155R71E104KE14J | Mouser | 81-GRM155R71E104KE4J | 0.025
C_0402_1uF_10V_X7R | C5, C7, C10, C13, C17, C18, C21, C23, C31, C38, C39, C42, C45, C49, C50, C53, C55, C57, C59, C61, C64, C65, C68, C69, C72, C75, C81, C99, C100, C106, C119, C121, C130, C131, C132, C134, C135, C137, C138, C139, C148, C149 | CAPC1005X06 | .C_0402_1uF_X7R_10V | 42 | Murata | GCM155C71A105KE38D | Mouser | 81-GCM155C71A105KE8D | 0.05
C_0402_10nF_25V_NP0 | C6, C35, C62, C93, C96, C140, C142 | CAPC1005X06 | .C_0402_10nF_25V_NP0 | 7 | Murata | GRM1555C1E103JE01J | Mouser | 81-GRM1555C1E103JE1J | 0.15
C_0603_10uF_16V | C8, C9, C15, C16, C19, C24, C25, C26, C32, C33, C40, C41, C44, C48, C51, C76, C77, C87, C90, C92, C94, C95, C97, C103, C107, C109, C111, C115, C117, C153, C154 | CAPC1608X09 | .C_0603_10uF_16V | 31 | Taiyo Yuden | EMK107BBJ106MA-T | Mouser | 963-EMK107BBJ106MA-T | 0.14
C_D8L12_470uF_25V | C47 | CAP-ELCO_D8L12mm | .C_D8L12_470uF_25V | 1 | Wurth | 860020474014 | Mouser | 710-860020474014 | 0.25
C_1206_47uF_10V | C82, C83, C110, C112, C114, C116, C146 | CAPC3216X18 | .C_1206_47uF_10V | 7 | Taiyo Yuden | LMK316ABJ476ML-T | Mouser | 963-LMK316ABJ476ML-T | 0.23
C_1206_100uF_6V3 | C88, C89, C101, C102, C145 | CAPC3216X18 | .C_1206_100uF_6V3 | 5 | Taiyo Yuden | JMK316ABJ107ML-T | Mouser | 963-JMK316ABJ107ML-T | 0.25
C_0402_47pF_50V | C104 | CAPC1005X06 | .C_0402_47pF_50V | 1 | Kemet | C0402C470K5GACTU | Mouser | 80-C0402C470K5G | 0.01
C_D8L12_680uF_10V | C150 | CAP-ELCO_D8L12mm | .C_D8L12_680uF_10V | 1 | Wurth | 860020274013 | Mouser | 710-860020274013 | 0.20
C_D8L12_1mF_6V3 | C151, C152 | CAP-ELCO_D8L12mm | .C_D8L12_1mF_6V3 | 2 | Nichicon | UVR0J102MPD1TD | Mouser | 647-UVR0J102MPD1TD | 0.25
D_SOD123W_710mV_1A | D1 | SODFL350X110-2N | .D_SOD123W_710mV_1A | 1 | Nexperia | PMEG10010ELRX | Mouser | 771-PMEG10010ELRX | 0.24
D_LED_0603_Amber | D3, D4, D5, D6 | DIOM1608X02N Orange | .D_LED_0603_Amber | 4 | Wuerth | 150060AS75000 | Mouser | 710-150060AS75000 | 0.12
D_LED_0603_Green | D7, D8, D13, D16, D17 | DIOM1608X02N Green | .D_LED_0603_Green | 5 | Wuerth | 150060VS55040 | Mouser | 710-150060VS55040 | 0.14
D_SOD523_370mV_500mA | D10, D11, D12, D14 | SODFL160X70-2N | .D_SOD523_370mV_500mA | 4 | On Semi | NSR05T30XV2T5G | Mouser | 863-NSR05T30XV2T5G | 0.18
J_T1x2_3.5mm_Screw | J1 | P_Phoenix_1984617 | .J_T1x2_3.5mm_Screw | 1 | Phoenix Contact | 1984617 | Mouser | 651-1984617 | 0.39
L_FB_0603_Z600R_1300mA | L1, L2 | INDC1608X08 | .L_FB_0603_Z600R_1300mA | 2 | Murata | BLM18KG601SN1D | Mouser | 81-BLM18KG601SN1D | 0.05
L_NR3015T1R5M | L3 | INDP3030X15N | .L_NR3015T1R5M | 1 | Taiyo Yuden | NR3015T1R5N | Mouser | 963-NR3015T1R5N | 0.20
L_NR3015T150M | L5, L8, L9, L12 | INDP3030X15N | .L_NR3015T150M | 4 | Taiyo Yuden | NR3015T150M | Mouser | 963-NR3015T150M | 0.23
SMS-455Cover | M1, M3 |  | SMS-455Cover | 2 | LeaderTech | SMS-455-N-C | Mouser | 861-SMS-455-N-C | 0.34
SMS-455FrameOpen | M2 | SMS-455F - Neighbour | SMS-455FrameOpen | 1 | LeaderTech | SMS-455-N-F | Mouser | 861-SMS-455-N-F | 1.87
SMS-455Frame | M4 | SMS-455F | SMS-455Frame | 1 | LeaderTech | SMS-455-N-F | Mouser | 861-SMS-455-N-F | 1.87
BeagleBoneGreen | P1 |  | BeagleBoneGreen | 1 | Seeed Studio | 102010027 | RS-Online | 174-3279 | 39.19
P_JST_S4B_ZR-SM4A | P2 | P_JST_S4B-ZR-SM4A | .P_JST_S4B_ZR-SM4A | 1 | JST | S4B-ZR-SM4A-TF(LF)(SN) | Digikey | 455-1695-1-ND | 0.51
P_GCT_USB4125_GFA | P3 | P_GCT_USB4125-GF-A | .P_GCT_USB4125_GFA | 1 | GCT | USB4125-GF-A | Mouser | 640-USB4125-GF-A | 0.43
P_HDR_2x2_2.54mm_header | P6 | P_Pinheader_2x2_R2.54mm | .P_HDR_2x2_2.54mm_male | 1 | Amphenol | 861400042YO2319LF | Mouser | 649-86140042YO2319LF | 0.12
Beaglebone P8 | P8 | P_Pinheader_2x23_R2.54mm_LongPinHeader | Beaglebone P8 | 1 | Samtec | SSQ-123-03-G-D | Digikey | SAM1196-23-ND | 6.45
Beaglebone P9 | P9 | P_Pinheader_2x23_R2.54mm_LongPinHeader | Beaglebone P9 | 1 | Samtec | SSQ-123-03-G-D | Digikey | SAM1196-23-ND | 6.45
P_HDR_2x9_2.54mm_header | P10, P11 | P_Pinheader_2x9_R2.54mm_male | .P_HDR_2x9_2.54mm_male | 2 | Amphenol FCI | 10129381-918001BLF | Mouser | 649-1012938191801BLF | 0.28
R_0402_1k | R1, R3, R5, R8, R14, R15, R18, R24, R27, R55, R56, R57, R59, R60, R61, R62, R63, R64, R65, R66, R67, R68, R79, R80, R82, R83, R91, R92, R93, R94, R112, R113, R124, R125, R126, R127 | RESC1005X04 | .R_0402_1k | 36 | Panasonic | ERJ-2GEJ102X | Mouser | 667-ERJ-2GEJ102X | 0.02
R_0402_2R | R2, R129 | RESC1005X04 | .R_0402_2R | 2 | Panasonic | ERJ-2GEJ2R0X | Mouser | 667-ERJ-2GEJ2R0X | 0.02
R_0402_10k | R4, R6, R7, R11, R13, R17, R23, R26, R28, R87, R88, R89, R90, R95, R96, R97, R102, R103 | RESC1005X04 | .R_0402_10k | 18 | Panasonic | ERJ-2GEJ103X | Mouser | 667-ERJ-2GEJ103X | 0.02
R_1206_2R_0.25% | R9, R21 | RESC3116X06 Shunt | .R_1206_2R_0.25% | 2 | Yageo | RT1206CRD072RL | Mouser | 603-RT1206CRD072RL | 0.35
R_0402_33R | R10, R16, R22, R69, R70, R71, R72, R73, R74, R75, R76, R77, R78, R81, R84, R85, R86 | RESC1005X04 | .R_0402_33R | 17 | Panasonic | ERJ-2GEJ330X | Mouser | 667-ERJ-2GEJ330X | 0.02
R_0402_210R_0.1% | R12, R29, R130 | RESC1005X04 | .R_0402_210R_0.1% | 3 | Yageo | RT0402BRD07210RL | Mouser | 603-RT0402BRD07210RL | 0.19
R_0402_10R | R19, R58 | RESC1005X04 | .R_0402_10R | 2 | Panasonic | ERJ-2GEJ100X | Mouser | 667-ERJ-2GEJ100X | 0.02
R_0402_100R | R20 | RESC1005X04 | .R_0402_100R | 1 | Panasonic | ERJ-2GEJ101X | Mouser | 667-ERJ-2GEJ101X | 0.02
R_0402_5k1_1% | R25, R107 | RESC1005X04 | .R_0402_5k1_1% | 2 | Panasonic | ERJ-2RKF5101X | Mouser | 667-ERJ-2RKF5101X | 0.02
R_0402_100k_1% | R30, R31, R32, R33, R34, R35, R36, R37, R38, R40, R42, R43, R44, R45, R46, R47, R48, R49, R50, R52, R54, R98, R101, R105, R111, R128 | RESC1005X04 | .R_0402_100k | 26 | Panasonic | ERJ-2RKF1003X | Mouser | 667-ERJ-2RKF1003X | 0.02
R_0402_470R | R39, R41, R51, R53, R100, R106, R109, R114, R115, R116, R117, R118, R119, R120, R121, R122, R123 | RESC1005X04 | .R_0402_470R_1% | 17 | Panasonic | ERJ-2RKF4700X | Mouser | 667-ERJ-2RKF4700X | 0.028
R_0402_24k | R99 | RESC1005X04 | .R_0402_24k | 1 | Panasonic | ERJ-2GEJ243X | Mouser | 667-ERJ-2GEJ243X | 0.02
R_0402_680k_1% | R104 | RESC1005X04 | .R_0402_680k_1% | 1 | Panasonic | ERJ-2RKF6803X | Mouser | 667-ERJ-2RKF6803X | 0.02
R_0402_240k_1% | R108, R110 | RESC1005X04 | .R_0402_240k_1% | 2 | Panasonic | ERJ-2RKF2403X | Mouser | 667-ERJ-2RKF2403X | 0.02
R_0402_0R_1% | R131, R132 | RESC1005X04-SEL | .R_0402_0R_1%_SEL | 2 | Panasonic | AC0402FR-070RL | Mouser | 603-AC0402FR-070RL | 0.02
T_BSH105 | T1, T2 | SOT95P230X110-3N | .T_BSH105 | 2 | Nexperia | BSH105,215 | Mouser | 771-BSH105215 | 0.21
OPA2388 | U1, U5 | TSOP65P490X110-8N | OPA2388 | 2 | TI | OPA2388IDGKR | Mouser | 595-OPA2388IDGKR | 2.63
UA_DAC8562-DSC | U2, U8 | PSON50P300X80_HS-11N | DAC8562-DSC | 2 | TI | DAC8562SDSCR | Mouser | 595-DAC8562SDSCR | 6.73
AD8421B | U3, U7 | TSOP65P490X110-8N | AD8421B | 2 | Analog | AD8421BRMZ | Mouser | 584-AD8421BRMZ | 8.10
ADS8691 | U4, U6, U9 | TSOP65P640X120-16N | ADS8691 | 3 | TI | ADS8691IPWR | Mouser | 595-ADS8691IPWR | 8.5
UA_OPA189-DBV | U10 | SOT95P280X145-5N | OPA189-DBV | 1 | TI | OPA189IDBVR | Mouser | 595-OPA189IDBVR | 2.02
UD_74LVC2T45-GT | U11, U12, U23, U24, U25, U26, U27, U28, U29 | SON50P100X50_HS-9N | 74LVC2T45GT | 9 | Nexperia | 74LVC2T45GT,115 | Mouser | 771-74LVC2T45GT115 | 0.37
UD_NLAS4684-FC | U13, U33, U35 | BGA12C50P4X3_196X146X65 | NLAS4684-FC | 3 | ON Semi | NLAS4684FCT1G | Mouser | 863-NLAS4684FCT1G | 0.80
TC7WH08FK | U14 | TSSOP50P310X80-8N | TC7WH08FK | 1 | Toshiba | TC7WH08FK,LJ(CT | Mouser | 757-TC7WH08FKLJCT | 0.24
HCT2G04 | U15 | SOT65P210X110-6N | HCT2G04 | 1 | Nexperia | 74HC2G04GW,125 | Mouser | 771-HC2G04GW125 | 0.21
UA_OPA388-DBV | U16, U32 | SOT95P280X145-5N | OPA388-DBV | 2 | TI | OPA388IDBVR | Mouser | 595-OPA388IDBVR | 1.80
UD_CAT24C256-HU | U17 | PSON50P300X55_HS-9N | CAT24C256-HU4 | 1 | ON Semi | CAT24C256HU4IGT3 | Mouser | 863-CAT24C256HU4IGT3 | 0.36
TPL5010 | U18 | SOT95P280X100-6N | TPL5010 | 1 | TI | TPL5010DDCR | Mouser | 595-TPL5010DDCR | 0.62
LP2989-5.0 | U19 | TSOP65P490X110-8N | LP2989-5.0 | 1 | TI | LP2989AIMM-5.0/NOPB | Mouser | 926-LP2989AIMM50NOPB | 2.05
MP3221 | U20 | SOT95P280X100-6N | MP3221 | 1 | MPS | MP3221GJ-Z | Mouser | 946-MP3221GJ-Z | 1.33
LP2989-3.3 | U21 | TSOP65P490X110-8N | LP2989-3.3 | 1 | TI | LP2989IMM-3.3/NOPB | Mouser | 926-LP2989IMM3.3NOPB | 2.27
LT3487 | U22 | PSON50P300X100_HS-11N | LT3487 | 1 | Analog | LT3487EDD#TRPBF | Mouser | 584-LT3487EDD#TRPBF | 2.72
UD_74HC4066-BQ | U30, U31 | PQFN50P250X300X100_HS-15N | 74HC4066BQ | 2 | Nexperia | 74HC4066BQ,115 | Mouser | 771-HC4066BQ115 | 0.27
UD_PI5A4158ZA | U34, U36, U37, U38, U39, U40, U41 | SON50P100X80_HS-13N | PI5A4158ZA | 7 | Diodes Inc | PI5A4158ZAEX | Mouser | 729-PI5A4158ZAEX | 0.36

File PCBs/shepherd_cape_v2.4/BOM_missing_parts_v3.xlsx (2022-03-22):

Distributer | Manufacturer | Name | Manufacturer PN | Price [€] | Distributer PN | Quantity
Mouser - kai | nordic | nRF-PPK2 | nRF-PPK2 | 87.54 € | 949-NRF-PPK2 | 2
Mouser | Diodes Inc | PI5A4158ZAEX | PI5A4158ZAEX | 0.36 € | 729-PI5A4158ZAEX | 300
Mouser | Yageo | 470R Ersatz | RC0402FR-13470RL | 0.02 € | 603-RC0402FR-13470RL | 600
Mouser | Yageo | 0R Ersatz | AC0402FR-070RL | 0.02 € | 603-AC0402FR-070RL | 200
Mouser | Murata | 100nF | GRM155R71E104KE14J | 0.03 € | 81-GRM155R71E104KE4J | 2000
Mouser | Murata | 10nF | GRM1555C1E103JE01J | 0.15 € | 81-GRM1555C1E103JE1J | 300
Mouser | Vishay | DG612EEN | DG612EEN-T1-GE4 | 1.31 | 78-DG612EEN-T1-GE4 | 10
Mouser | Vishay | DG2501DB | DG2501DB-T2-GE1 | 1.37 | 78-DG2501DB-T2-GE1 | 10

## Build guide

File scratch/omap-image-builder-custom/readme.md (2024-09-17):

## Install

git clone https://github.com/RobertCNelson/omap-image-builder
cd ./omap-image-builder
rm -rf ./git

For Debian based distros the prereqs are:

- m4
- debootstrap
- debootstick
- qemu-system-arm (+ many dependencies)
- chrootuid (?? probably not)
- bash-completion (convenience)
- git
- sbuild (just a guess)
- [buildroot-reqs](https://buildroot.org/downloads/manual/manual.html#requirement) (probably not needed)
- qemubuilder (+ many dependencies)
- qemu-user-static
- crossbuild-essential-armhf
- coreutils
- sbuild-qemu
- qemu-utils
- pbuilder
- cdebootstrap
- zstd
- schroot
- tree  (definitely)

## Run Ubuntu 20.04 Focal

```Shell
./RootStock-NG.sh -c rcn-ee.net-console-ubuntu-focal-v5.10-ti-armhf

rm -rf ./ignore
cd deloy/ubu

sudo ./setup_sdcard.sh --img-2gb am335x-ubuntu-20.04.5-console-armhf-2023-03-14 --dtb beaglebone --distro-bootloader --enable-cape-universal --enable-uboot-disable-pru --enable-bypass-bootup-scripts

xz -v6 am335
#  ⇾ 4 MB/s, -v6 got ~8 MB/s
mv am ~/

# ⇾ should yield 318 M

sudo du -hc --max-depth=1 ./

scp service@141.76.39.100:/home/service/am335x-ubuntu-20.04.5-console-armhf-2023-03-11-2gb.img.xz /mnt/f/
```

## Run Ubuntu 22.04 Jammy

```Shell
nano ./configs/neslab-ubuntu-jammy-console-armhf.conf

./RootStock-NG.sh -c neslab-ubuntu-jammy-console-armhf

final name "shepherd-ubuntu-20.04.5-console-armhf-2023-03-10-2gb.img.xz"

scp service@141.76.39.100:/home/service/omap-image-builder/deploy/ubuntu-20.04.5-console-armhf-2023-03-10/ubuntu-20.04.5-console-armhf-2023-03-10-2gb-2gb.img.xz ./
```

## run Ubuntu 22.04 focal (frankenstein)

```
./RootStock-NG.sh -c neslab-ubuntu-focal-console-v4.19-ti-armhf
# ⇾ does NOT work as used ubuntu image is determined by deb_codename
```

## slim down the ubuntu image

wireless - removable

    bluetooth
    hostapd
    iw
    wpasupplicant

    bb-wl18xx-firmware
    bb-wlan-defaults

functionality not needed

    btrfs-progs
    gnupg
    hexedit
    less            (⇾ nano)
    pastebinit
    vim

    bb-bbai-firmware
    bb-u-boot-am57xx-evm
    sancloud-firmware

additionally unneeded (to test)

    linux-firmware      (+ comment-out "include_firmware")
    libiio-utils        (industrial IO Subsystem)
    cloud-guest-utils   (TODO, depends on fdisk, gdisk, python3)
    wireguard-tools

switch to older kernel by default (focal)

    bbb.io-kernel-4.19-ti
    linux-image-4.19.94-ti-r73
    4.19.94-ti-r73
    4.19-ti
    cmem = 4.16.00.01
        ⇾ installs ti-cmem-{version}
        https://github.com/rcn-ee/ti-cmem
        https://github.com/rcn-ee/ipc-ludev
        TODO: 4.20.00.01 could still be ok?

add functionality

    zstd

result

    xz-v6   raw
    323     1396        official repo
    319 MB  1363 MB     home-build, unchanged   (50 MB ram usage)
    150      578        without (1/2 of) above
    147      571        apply above (except cloud-guest)
    139      547        switch to 4.19           ⇾ works!

## switch apt to jammy (dirty)

base: latest 4.19 image

```Shell
sudo nano /etc/apt/sources.list

# - start with 580 mb used, 47 mb ram

# ⇾ replace focal with jammy on official repos
#    - ends with 760 mb used
#    - python 3.10.6

# ⇾ replace with lunar
#    - ends with 893 mb used, 41 mb ram
#    - python 3.11.1 & 3.10.9 ?

sudo do-release-upgrade -d

shepherd install
apt installs python3-numpy 1.24.2-1
# but pip install shepherd-package installs numpy again - with full compile
```

| Package                  | Version     |
|--------------------------|-------------|
| dbus-python              | 1.3.2       |
| decorator                | 5.1.1       |
| distlib                  | 0.3.6       |
| filelock                 | 3.9.0       |
| gevent                   | 22.10.2     |
| greenlet                 | 2.0.1       |
| h5py.-debian-h5py-serial | 3.7.0       |
| Mako                     | 1.2.4.dev0  |
| Markdown                 | 3.4.1       |
| markdown-it-py           | 2.1.0       |
| MarkupSafe               | 2.1.2       |
| mdurl                    | 0.1.2       |
| msgpack                  | 1.0.3       |
| netifaces                | 0.11.0      |
| numpy                    | 1.24.2      |
| olefile                  | 0.46        |
| Pillow                   | 9.4.0       |
| pip                      | 23.0.1      |
| platformdirs             | 3.0.0       |
| py                       | 1.11.0      |
| Pygments                 | 2.14.0      |
| PyGObject                | 3.43.1.dev0 |
| pymacaroons              | 0.13.0      |
| PyNaCl                   | 1.5.0       |
| python-apt               | 2.5.3       |
| PyYAML                   | 6.0         |
| pyzmq                    | 24.0.1      |
| rich                     | 13.3.1      |
| scipy                    | 1.10.1      |
| setuptools               | 67.6.0      |
| six                      | 1.16.0      |
| ubuntu-advantage-tools   | 8001        |
| virtualenv               | 20.20.0     |
| wheel                    | 0.38.4      |
| zope.event               | 4.4         |
| zope.interface           | 5.5.2       |

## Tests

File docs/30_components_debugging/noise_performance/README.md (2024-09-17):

# Cape Noise Performance

## Problem

- Beaglebone offers noisy SYS_5V0 - TODO: add Vpp num
- POE is also noisy - TODO: add Vpp num
- shepherd shows residues of voltage spikes in target voltage
    - Solved: confirmed to be due to a "transmitting" usb-hub 50 cm away from test-setup (not powering anything)

## Setup

- BBGreen with Shepherd-PCB, Output VTarget set to 3V
- scope: rigol ds1104z, 100 MHz, calibrated, compensated probes, up-to-date firmware

- 50 cm radius free of additional metal
- Power-Supplies
    - setup1: 5V to BB via benchsupply with 1mF on input
    - setup2: as setup 1, but shepherd 5V and 3v3 powered by keithley sourcemeter, 1m 4-Port Cables, not buffered by Cap
    - setup3: BB powered by NoName POE-Splitter (EC-PD0520USB)
    - setup4: BB powered by TP-Link POE-Splitter (TL-POE10R), buffered by 1 mF on Input
- Measurement
    - scope input set to AC to analyze ripple, internal 20 MHz low pass active
    - probe set to 1x for low noise
    - probe connected with short ground-loop to closest GND
    - timebases /div (mostly): 50 ms, 10 ms, 1 ms, 100 us, 10 us, 1 us, 100 ns
    - voltage range: lowest setting without clipping, mostly 1 mV/div
    - scope-math: Voltage-peak-peak, frequency
- Scope-Screenshots (DS1Z_Quickprint#.png) are not linked or included here, only referenced for each measurement (./media_noise/)

### Scope Noise with grounded signal-input

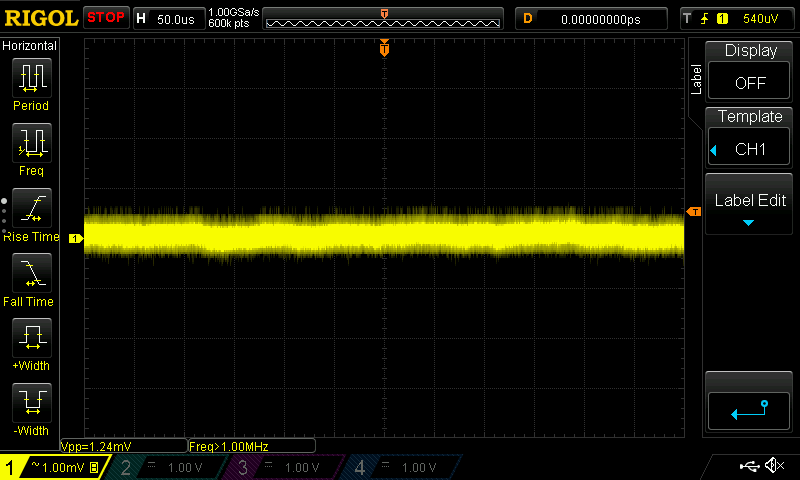
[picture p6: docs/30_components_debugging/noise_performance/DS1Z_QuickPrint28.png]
noise


## Measurements

- Probe Signal shorted to ground (noise floor)
    - Vpp = 1.20 mV
    - no abnormalities or standing waves
    - QuickPrint 26-31
- **SETUP 2**
- A5V (setup2) - on biggest cap after regulator
    - Vpp = 2.10 mV
    - 1.3 MHz Ripple (1.72mVpp)
    - QuickPrint 32-36
- 10V (setup2) - on biggest cap after regulator
    - Vpp = 3.40 mV
    - 7 kHz Ripple,
    - QuickPrint 37-41
- VTargetA = 3.3 V (setup2), 1k Load
    - Vpp = 1.90 mV
    - no abnormalities or standing waves
    - QuickPrint 42-46
- VTargetA = 3.3 V (setup2), no load
    - Vpp = 1.72 mV
    - no abnormalities or standing waves
    - QuickPrint 47
- VTargetB = 3.0 V (setup2), no load
    - Vpp = 1.65 mV
    - no abnormalities or standing waves
    - QuickPrint 48-52
- SourceMeter 3V3 (setup2), ~ 4.06 mA Shepherd-Load, 4-Port-Meas
    - Vpp = 16.6 mV (unfiltered input)
    - no abnormalities, some switching noise
    - QuickPrint 53-57
- SourceMeter 5V0 (setup2), ~ 73.9 mA Shepherd-Load, 4-Port-Meas
    - Vpp = 20.4 mV (unfiltered input)
    - no abnormalities, some switching noise
    - QuickPrint 63-67
- BBone 3v3 (setup2) - on pinheader, shepherd not connected
    - Vpp = 46 mV
    - no abnormalities, some switching noise 20 kHz & 333 kHz
    - QuickPrint 58-62
- BBone SYS_5V / P9-7/8 (setup2) - on pinheader, shepherd not connected
    - Vpp = 145 mV
    - all kind of fragments from msec to nsec (50 ms & 1us view shows best)
    - QuickPrint 68-72
- BBone VDD_5V / P9-5/6 (setup2) - on pinheader, shepherd not connected
    - Vpp = 5.6 mV
    - minor abnormalities, 5Hz wave, 333 kHz switching fragments
    - QuickPrint 73-79
- **SETUP 1**
- VTargetA = 3.3 V (setup1), no load
    - Vpp = 1.8 mV
    - no abnormalities or standing waves
    - QuickPrint 80-87
- A5V (setup1) - on biggest cap after regulator
    - Vpp = 1.9 mV
    - no abnormalities, some ripple ~1.3 MHz, 1.6 mVpp
    - QuickPrint 101-106
- BBone 3v3 (setup1) - on pinheader
    - Vpp = 51 mV
    - switching noise 20 kHz, 250 kHz
    - QuickPrint 107-113
- BBone SYS_5V / P9-7/8 (setup1) - on pinheader
    - Vpp = 111 mV
    - switching noise 10 Hz, 50 Hz, 20 kHz, 333 kHz, 2.5 MHz
    - QuickPrint 114-120
- Bench Supply 5V (setup1) - 360 mA Load
    - Vpp = 37 mV
    - switching noise 10 Hz, 50 Hz, 2.5 kHz
    - QuickPrint 121-130
- Bench Supply 5V (setup1) - no Load
    - Vpp = 20 mV
    - switching noise 4 kHz
    - QuickPrint 131-137
- **SETUP 3**
- BBone 5V Input (setup3), TP-Link Poe
    - Vpp = 22 mV
    - switching noise 10 Hz, 50 Hz, 16 kHz, 256 kHz
    - QuickPrint 201-207
- VTargetA = 3.3 V (setup3), no load
    - Vpp = 2.7 mV
    - no abnormalities, but some oscillation around ~ 1 MHz
    - QuickPrint 208-215
- A5V (setup1) - on biggest cap after regulator
    - Vpp = 3.3 mV
    - no abnormalities, but some oscillation around 1.3 MHz
    - QuickPrint 216-224
- **SETUP 4**
- BBone 5V VCC P9-5/6 (setup4), NoName Poe
    - Vpp = 7.6 mV
    - heavy switching noise ~ 75 kHz
    - QuickPrint 225-232
- VTargetA = 3.3 V (setup4), no load
    - Vpp = 12.2 mV
    - heavy switching noise ~75 kHz
    - QuickPrint 233-239
- A5V (setup4) - on biggest cap after regulator
    - Vpp = 11 mV
    - ramps with 50 kHz and the additional switching noise
    - QuickPrint 240-246
- **Setup1 - Tuning InAmp**
- VTargetA = 3.3V, 1k Load
    - Vpp = 1.9 mV
    - some oscillations at 145 kHz - 1 MHz
    - QuickPrint 301-307
- TP2
    - Vpp = 1.3 mV
    - not enough detail, but looks like noisefloor
    - QuickPrint 308
- TP5 - InAmp Output
    - Vpp = 110 mV
    - some oscillation just shy of 1 MHz
    - QuickPrint 309-318
- 10V - over biggest Cap
    - Vpp = 3.6 mV
    - some oscillation at 10 kHz
    - QuickPrint 319-324
- -6V - over biggest Cap
    - Vpp = 3.4 mV
    - some oscillation at 1.3 MHz
    - QuickPrint 325-330
- **MOD**: 8.2 OHm right before 1 Ohm Shunt
- TP5 - InAmp Output
    - Vpp = 16.4 mV
    - no abnormalities
    - QuickPrint 331-336
- Over 1 Ohm Shunt
    - Vpp = 2.24 mV
    - no abnormalities
    - QuickPrint 338
- Over 1 Ohm Shunt
    - Vpp = 2.24 mV
    - no abnormalities
    - QuickPrint 338
- **MOD**: 1k on InAmp-Output
- TP5 - InAmp Output
    - Vpp = 12.6 mV
    - no abnormalities
    - QuickPrint 339-344
- **MOD**: 100 nF over InAmp Input
- Over 1 Ohm Shunt
    - Vpp = 2.36 mV
    - oscillations at 380 kHz
    - QuickPrint 345-351
- TP5 - InAmp Output
    - Vpp = 11.5 mV
    - no abnormalities
    - QuickPrint 352-357

## Analysis

- disclaimer
    - some noise is very close to the scopes lower threshold (~ 1.2 mVpp)
    - A5V-LDO should have ~ 18 uV RMS-Noise with 60 dB Ripple Rejection (but show with higher noise)
    - ⇾ measurements can't be trusted when looking at individual values, but comparisons should be valid
    - amplifying active probe should be preferred
- A5V and VTargetA are very similar ⇾ further analysis will take maximum of these two
- setup comparison (worst to best)
    - setup4 (NoName POE) shows heavy artifacts, Noise VTarget = 12 mVpp
    - setup3 (TPLink POE) shows some oscillations, Noise A5V = 3.3 mVpp
    - setup2 (Shepherd powered by sourcemeter) shows minor ripple, noise A5V = 2.1 mVpp
    - setup1 (benchPowered BB) shows minor ripple, Noise A5V = 1.9 mVpp
- Sys_5V-Line is surprisingly noisy, but has limited influence on VTarget
- 10 V / -6 V has some 7 - 20 kHz Ripple ⇾ most likely bad for InAmp

## Conclusion / Mitigations

- BB-Power should be avoided
    - switch to VDD_5V (less noisy) instead of sys-5v ⇾ NOT POSSIBLE
    - Sys-5V was already used in previous shepherd pcb
    - avoid 3v3, generate on shepherd
    - allow manual "switch" to only use external power (move ferrite from sys_5V input to tap into 5v_ext-rail)
- InAmp - further improvement in noise
    - filter input, increase shunt to 10 Ohm, and 100nF parallel to the shunt brings 160 kHz Lowpass
    - filter output, 100k in line to ADC. ADC Pin has Capacitance of 5pF, Line ~1pF, brings ~300 kHz ⇾ option to solder a cap to Testpoint
- POE-Input
    - should be allowed to be > 5V, and filtered by ldo
    - **TP-Link TL-POE10R V5.0** is rated for 1A @ 9/12V, 2A @ 5V ⇾ ~ 10 W
- Side Note
    - TP-Link POE-Splitter has heat-issues at least when powering ~300@5V, ICs are Ok, but the input Cap (47uF 100V) gets also very warm ⇾ may shorten life-expectancy
    - there is no cheap alternative for this unit

## Stabilize Supplies

- Options for Stability / less noise
    - avoid switching regulators (noise usually >> 1 mVpp)
    - use LDO, specially low noise or ultra low noise ones (low noise LDOs are somewhere around 1 mVpp)
    - passive LC-LowPass at the End (
- 6V-Switching-Regulator had big opt-potential, 6x less Vpp-Switching-Noise
- +10/-6V-Regulator for InAmp
    - LT3487 is claiming low noise due to high frequency
    - regulator hysteresis should be around 6-7 mV for both rails (FBP has 7 m%/V, FBN has 1 mV/V Line Regulation)
    - measurements show ~ 3.4 mV after ferrite
- previous shepherd pcb
    - LM27762 has charge pump + ldo for 22 uV_RMS and 43 dB Ripple-Rejection, 1.5 mV/V Line and 34 uV/mA Load Regulation, but only outputs +-5V
- use additional very-low-noise LDOs (+10/-6V)
    - LP2985, 10V LDO, 30 uV_RMS, 45 dB Ripple Rejection
    - MIC5219 2.5 to 12 V LDO, 300 nV / sqrt(Hz), 75 dB Ripple Rejection, 9 m%/V Line Regulation
    - ADP7118, 2.7 to 20 V LDO, 11 uV_RMS, 50 dB Ripple Rejection, 15 m%/V Line Regulation
    - TPS723, -2.7 to -10 V LDO, 60 uV_RMS, 48 dB Ripple Rejection, 40 m%/V Line Regulation
    - Ricoh RP117x, -5.5 to -1 V, 80 dB Rejection, 16 uV_RMS,
    - LT3094, ultra low noise, 0 to -20V, 74 dB Rejection, 2.2 nV/sqrt(HZ), 0.8 uV_RMS
- InAmp AD8421
    - Inputs range from 0 to 5 V,
    - differential Voltage of 0 to 500 mV, Gain 10 ⇾ Power supply should be at least +9 V & -5 V, Ref = GND
    - differential Voltage of 0 to 50 mV, Gain 100 ⇾ Power supply should be at least +9 V & -5 V, Ref = GND
    - Diamond Plot: https://tools.analog.com/en/diamond/#difL=0&difR=0.05&difSl=0&gain=100&l=0&pr=AD8421&r=5&sl=0&tab=1&ty=2&vn=-5&vp=9&vr=0
    - there are two InAmps with a budget of ~ 74 mW, ~ 4.6 mA
- Positive Voltage ⇾ Voltage Doubler
    - LM266x not suited, no low noise
    - LM276x not suited, no low noise
- Negative Voltage ⇾ Inverter, Charge Pump
    - LM27761, 20 uV_RMS, 35 dB rejection, 1.5 mV/V Line and 4.6 uV/mA Load Regulation,
    - LTC1550, not suitable
    - TPS63710

## Verification of PI-Filter with Spectrum Analyzer

- SA
    - Rigol DSA 815 (9 kHz to 1.5 GHz) with tracking generator
    - 1 MHz Span, beginning at DC
- Filter
    - 15 uH shielded coil with 100 uF / 6.3 V on both sides
    - corner frequency: 4.1 kHz
- TG provided 0 dBm and input was calibrated to it
- open-input and filter in line showed no significant difference (no noticeable rise of the noise-floor)

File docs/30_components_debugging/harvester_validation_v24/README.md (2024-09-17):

# Harvester Frontend Validation

Test of various harvesting algorithms with a solar cell

- solar cell: IXYS SM101K09L
- lighting by philips LED 5.9 W 806 lm 2000-2700 K, 50 Hz
- lamp was ~ 10 cm above solar cell & the setup was covered with a white lampshade

Algorithms used:

- `mppt_opt`: very fast MPPT based on perturb & observe algorithm (Steps: 1 mV, 10 us)
- `mppt_bq`: MPPT of TI BQ-Converters for solar
- `cv20`: constant voltage of 2.0 V
- `ivcurve`: postponed harvesting by sampling ivcurves (voltage stepped as sawtooth-wave)

- [harvesting Profiles in detail](https://github.com/orgua/shepherd-datalib/blob/main/shepherd_core/shepherd_core/data_models/content/virtual_harvester_fixture.yaml)

Commands used:

```shell
shepherd-data extract-meta hrv.h5
shepherd-data plot hrv.h5 -e 10
shepherd-data plot hrv.h5 -e 1
shepherd-data plot hrv.h5 -e .1
```

## Harvested Energy

Values are calculated for a 10 s trace.

- `mppt_opt`: 36.720 mWs
- `mppt_bq`: 35.957 mWs
- `cv20`: 26.371 mWs
- `ivcurve`: 19.718 mWs

The files itself are published [here](https://drive.google.com/drive/folders/1ceOPv-2ci8bqypXK_aRST_ngh57R9bhM?usp=sharing).

## Plots

### OPT

The algorithm produces higher noise than the others due to the perturb-part to find a better set-point.

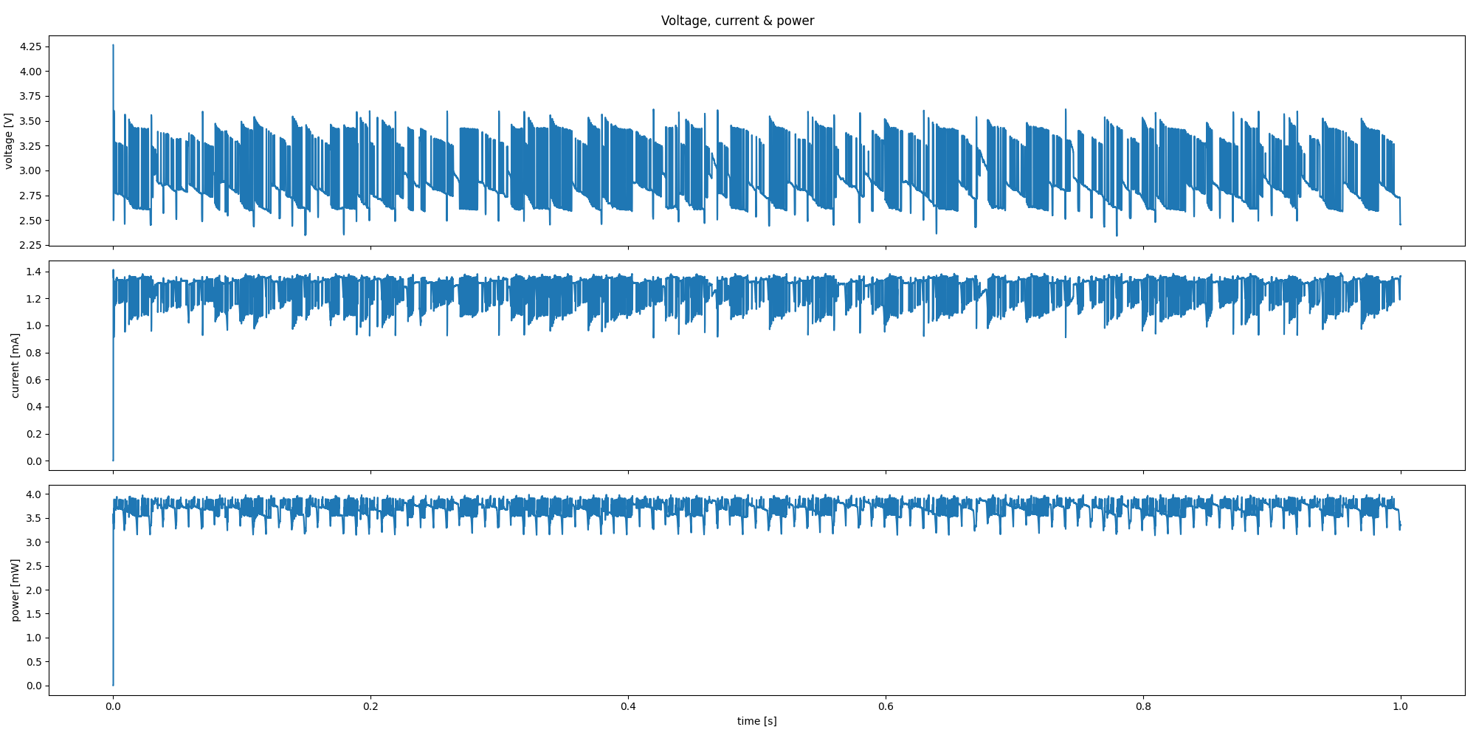
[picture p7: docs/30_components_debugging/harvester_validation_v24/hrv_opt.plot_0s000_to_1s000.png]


In more detail:

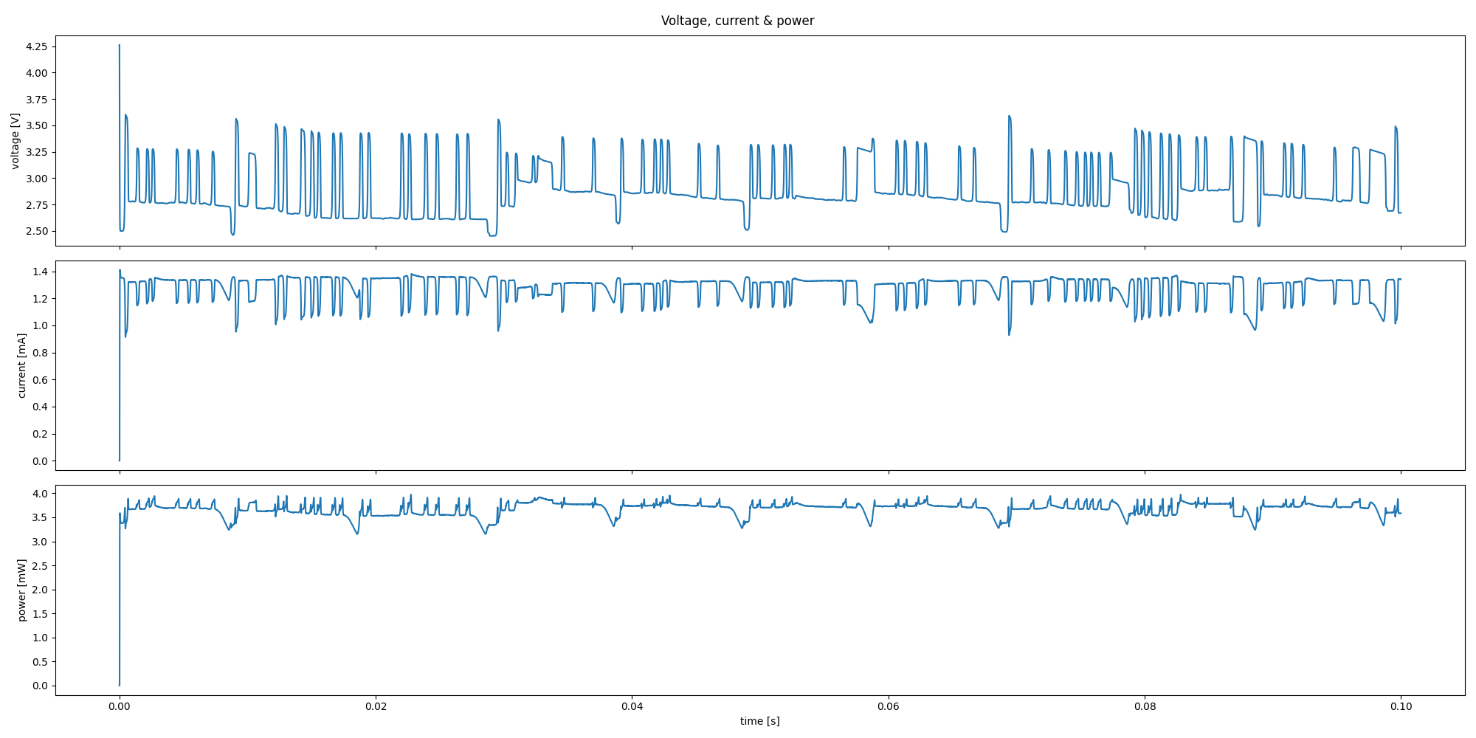
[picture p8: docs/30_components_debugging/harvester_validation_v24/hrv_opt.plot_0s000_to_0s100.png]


### BQ

BQ-Converters sample the open circuit voltage (VOC) every 16 s for about 256 ms and harvest at a set-point of 0.76 * VOC. First the voltage, then the current shows typical 50 Hz line flicker from the fast LEDs.

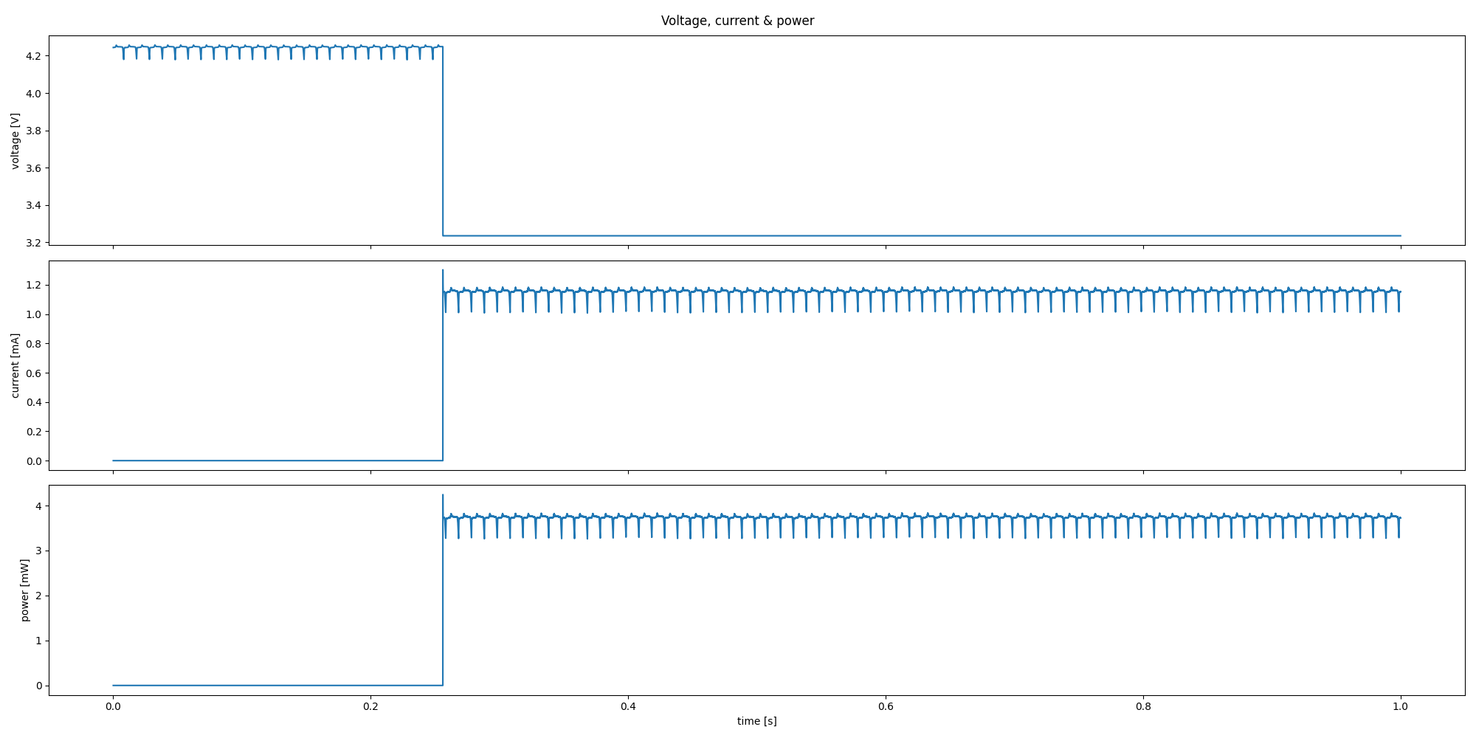
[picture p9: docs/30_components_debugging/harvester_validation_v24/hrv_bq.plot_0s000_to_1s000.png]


In more detail:

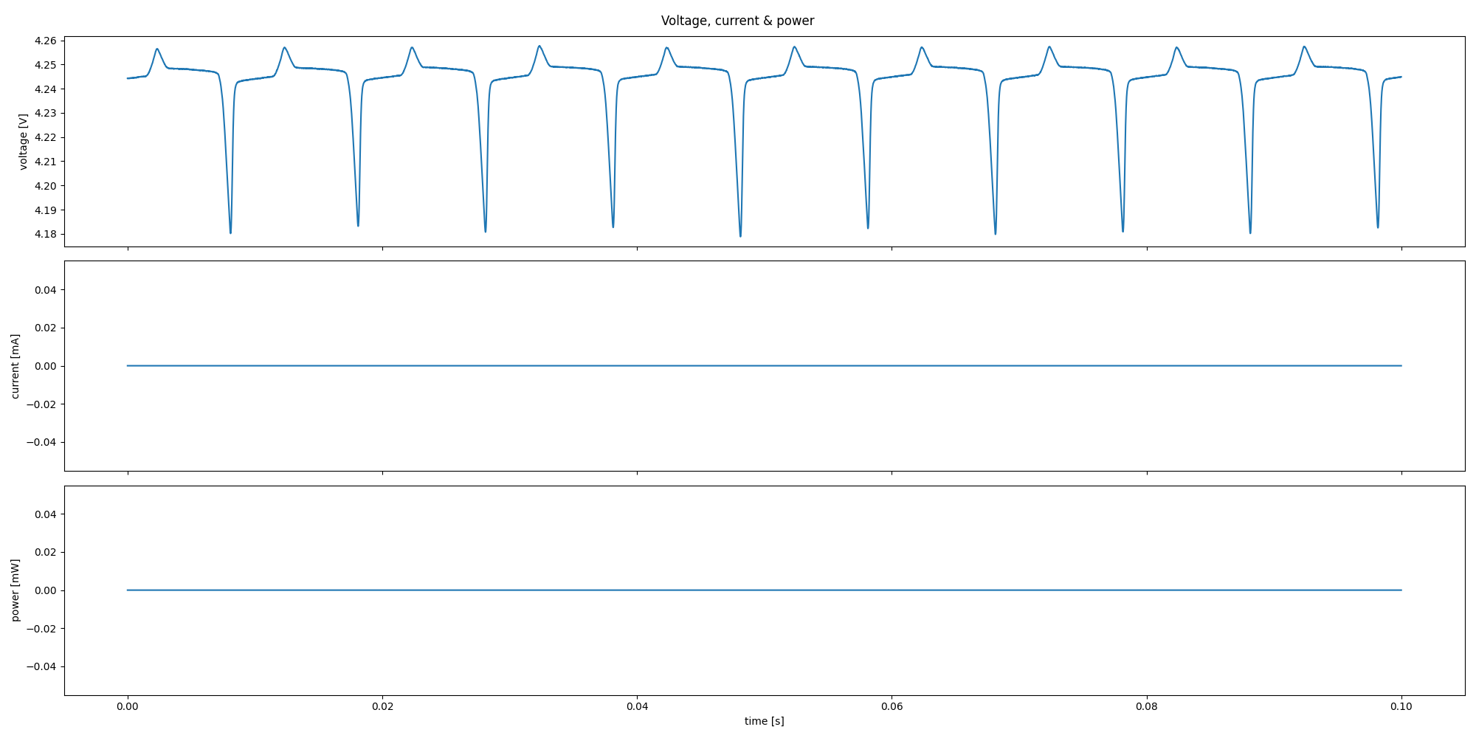
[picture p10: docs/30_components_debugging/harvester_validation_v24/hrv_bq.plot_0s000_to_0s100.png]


### CV20

Due to the constant voltage the 50 Hz line flicker is only visible in the current-plot.

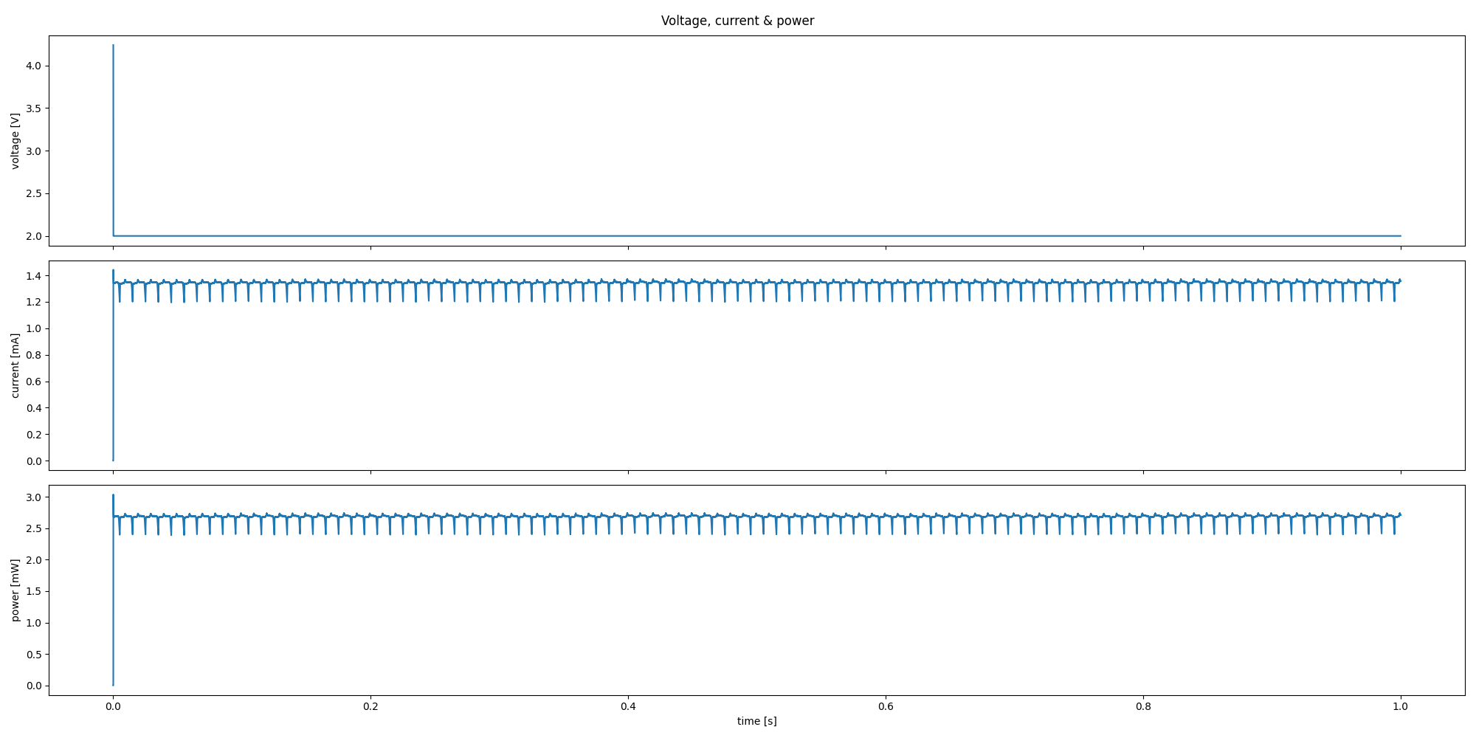
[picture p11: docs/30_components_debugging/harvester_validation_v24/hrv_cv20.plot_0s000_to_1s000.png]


In more detail:

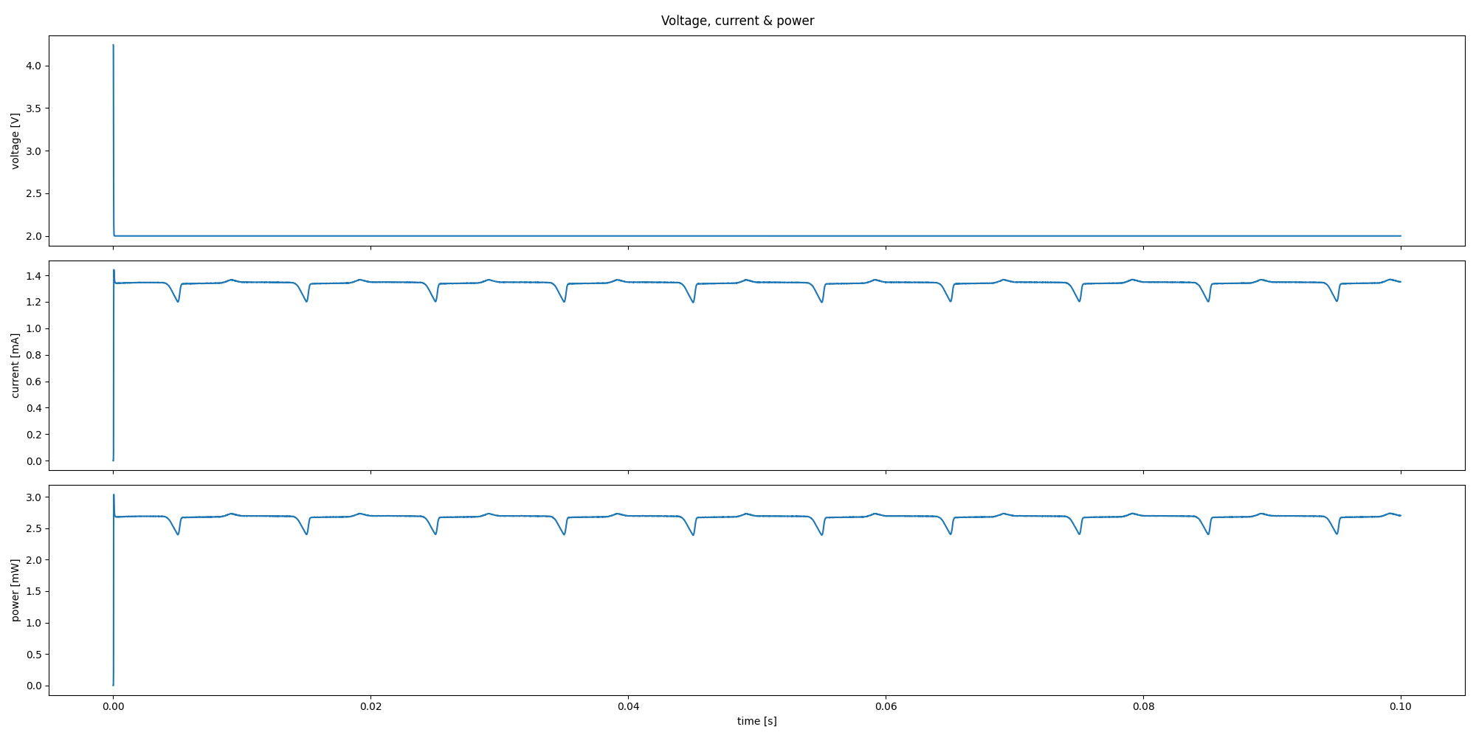
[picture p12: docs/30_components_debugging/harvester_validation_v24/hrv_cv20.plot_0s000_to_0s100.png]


### IVCURVE

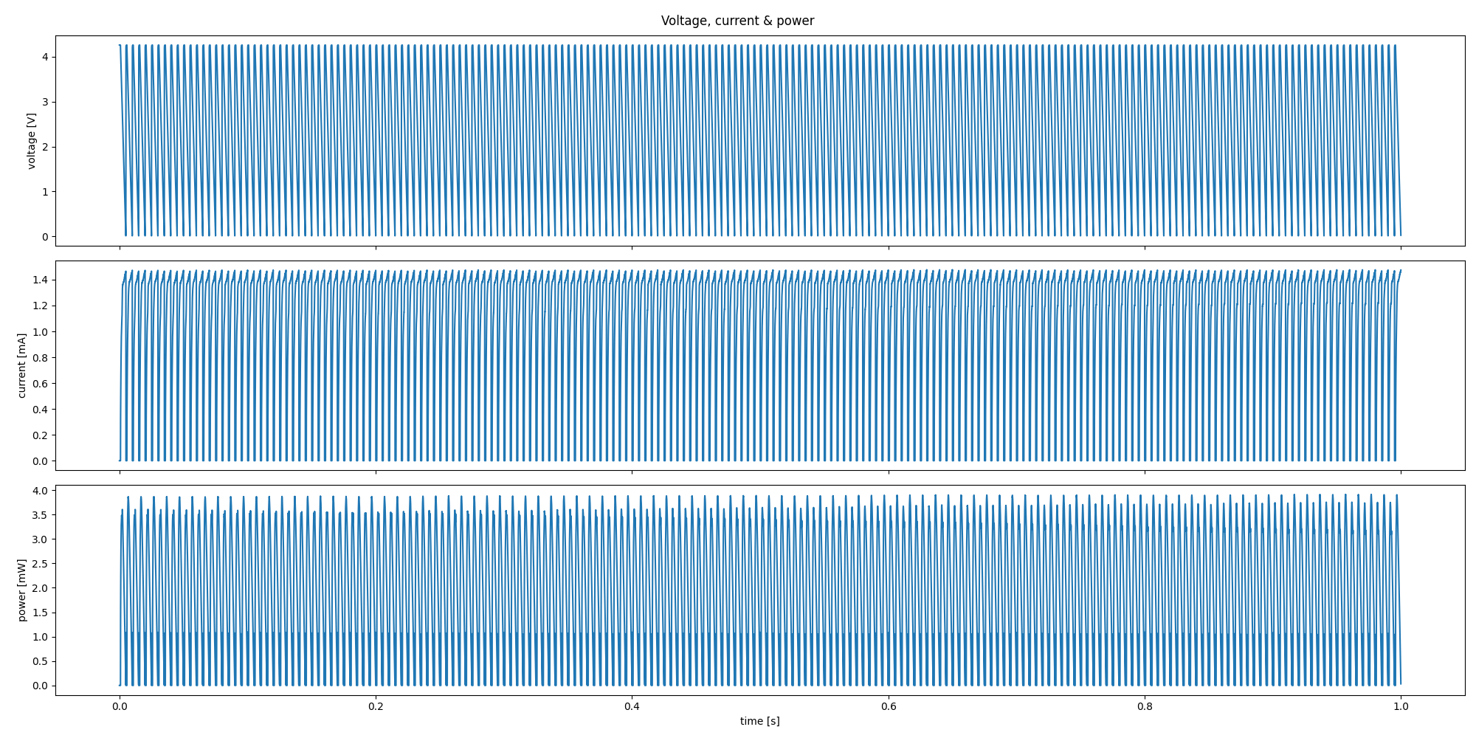
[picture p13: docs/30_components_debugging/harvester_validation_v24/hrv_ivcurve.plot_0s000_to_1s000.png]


In more detail:

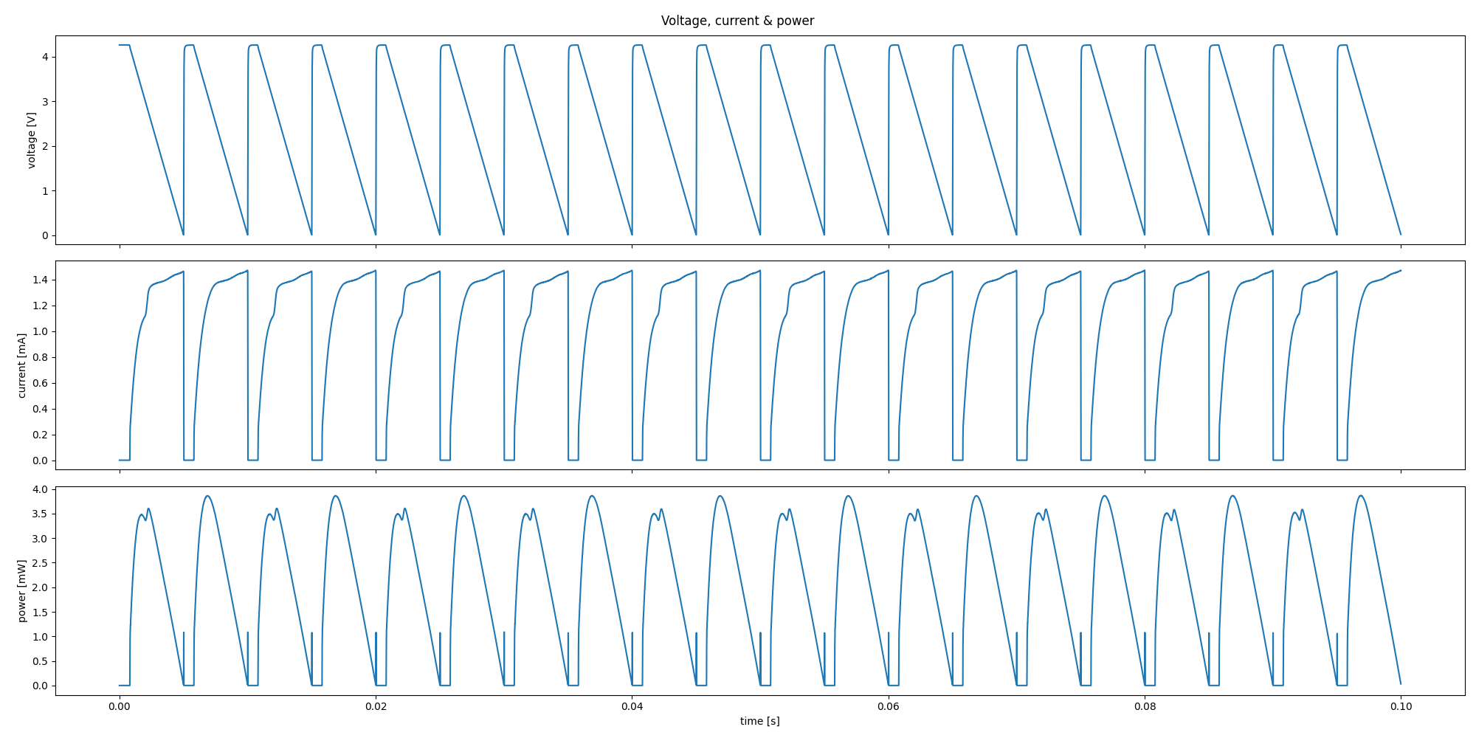
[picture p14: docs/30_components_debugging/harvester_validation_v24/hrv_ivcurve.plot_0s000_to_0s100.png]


Due to the 50 Hz line flicker every current ramp is uniquely shaped.

### Extra IVCurve-Processing

Using the given [vHarv-Example-code](https://github.com/orgua/shepherd-datalib/blob/main/shepherd_core/examples/vharvester_simulation.py) shows discrepancies when working with IVCurves.

```
E_out = 17.279 mWs -> cv20
E_out = 11.129 mWs -> cv10
E_out = 21.933 mWs -> mppt_voc
E_out = 17.069 mWs -> mppt_bq_solar
E_out = 17.069 mWs -> mppt_bq_thermoelectric
E_out = 38.276 mWs -> mppt_po
E_out = 28.517 mWs -> mppt_opt
```

Comparing that to the harvested energy from the beginning:

- `mppt_opt`: 36.720 mWs
- `mppt_bq`: 35.957 mWs
- `cv20`: 26.371 mWs
- `ivcurve`: 19.718 mWs

Losses of > 50% are visible.

### Extra Emu Comparison:

The `IVCurve`-Discrepancies also shows in an emulation of a BQ25570 with V_out = 3V and a 1 kOhm Resistor as Target.

#### MPPT_Opt into BQ25570

First the emulation is run on a real cape with `mppt_opt` as input where 36.72 mWs go in and 24.99 mWs are used, resulting in a ~50 % duty cycle:

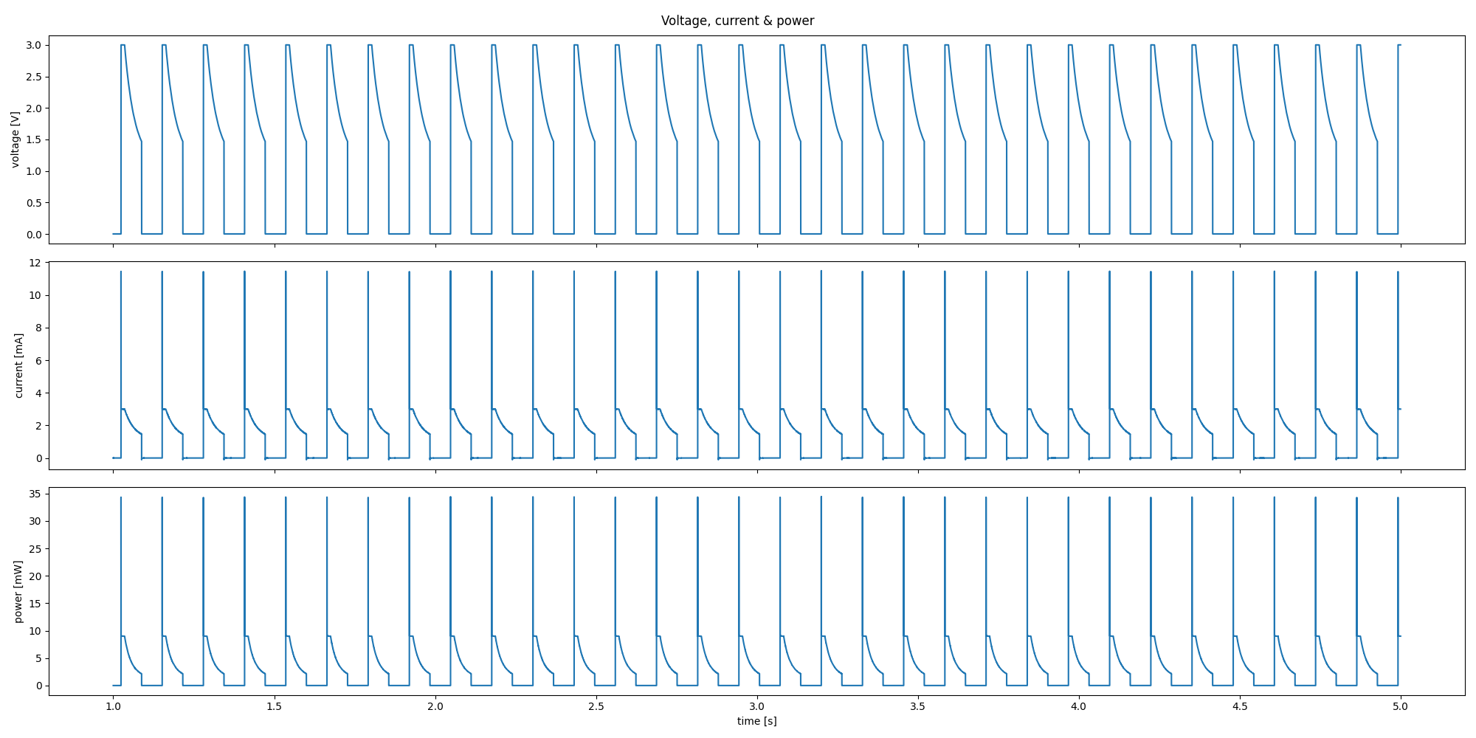
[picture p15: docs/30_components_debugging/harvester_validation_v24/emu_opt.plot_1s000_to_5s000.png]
emu with mppt_opt with bq


Simulating the target-resistor by using the python-implementation of the vSource will produce almost the exact same graph:

sim with mppt_bq

Comparison:

- input = 36.72 mWs
- emu output = 24.99 mWs
- sim output = 24.54 mWs

The simulation is missing the transient spikes from the HIL-emulation.

#### IVCurve into BQ25570

The same setup & config running with `ivcurve`-input, where only 10.54 mWs are used and the duty cycle is much lower and irregular:

emu with ivcurve

The simulation shows a more regular pattern:

sim with mppt_bq from ivcurve

Comparison:

- emu output = 10.54 mWs
- sim output = 10.64 mWs

The simulation shows a higher activation-count (20 vs 17 in 4 s). The HIL-Emulation shows a slightly different behavior that manifest in a larger 3V plateau.

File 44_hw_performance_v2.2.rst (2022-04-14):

HW Performance v2.2
=====================

Hardware
--------

- 8 Capes without Recorder, produced by Egas
- Serialnumbers
    - unknown num -> kai
    - 1191022, -23, -25, -27 -> kai
    - 1191029 -> debug-setup
- lend out to kai
    - 1 Cape with pinheader (unknown number)
    - 4 Capes with Long PinSocket (1022, 1023, 1025, 1027)
    - 2 + 1 + 3 Targets

Initial Test for Functionality
------------------------------

- visual inspection OK
- External powered single cape (current limited)
    - disabled cape -> draws 0 mA @ 5 V
    - 35 mA @ 5 V when EN-Pin is Pulled Up with 3 V
    - -> no unsual behaviour
- BB powered by benchsupply 5.1 V, ~ 350 - 400 mA
- Shepherd powered by BB, VIn 5.08V
- Main Voltages on enabled Cape
    - A5V/L5V 	-> 5.000 V    	Should be Spot On
    - A3V/L3V3 	-> 3.300 V    	Should be Spot On
    - 6V 	-> 5.38 V		    [5.29; 5.47] V with 1% Res
    - 10V 	-> 9.73 V		    [9.56; 9.90] V with 1% Res
    - -6V 	-> -6 V		        [5.94; 6.06] V with 1% Res
- calibration with 10 uF (1206, 25 VMax, 16 nA Leak) on both Ports
- Generated Voltages on Target Ports -> deviation is ~ 0.1 mV
- ADC Current-Readout is noisy, despite 10 uF Buffer
- GPIO pass-through:
    - gpio 0-8 and BATOK to TA & TB
    - unconnected pru-pins (p8-41to44) are not reporting activity -> fixed
- GPIO-Speed-Test by programming a target

Capes - fixed and tested
------------------------------

- 1191022: with boot-fix, faster essential gpio, stabile current-meas, stabile V_IO, gpio0 has also speed-fix
    - was used for debugging, some resistors are replaced instead of stacked during modding
- 1191023: with boot-fix, faster essential gpio, stabile current-meas, stabile V_IO
    - 3v3 is a bit off with 3.275 V
- 1191025: with boot-fix, faster essential gpio, stabile current-meas, stabile V_IO
- 1191027: with boot-fix, faster essential gpio, stabile current-meas, stabile V_IO
    - 3v3 is a bit off with 3.286 V
- 1191029: boot-fix, stabile V_IO

Debug-Investigation on 1191022
------------------------------

- BB still fails to boot when P8-41to44 are connected to cape -> lines are separated by a analog switch?!?
    - switch is powered by L3V3 ?!?
    - drilling out the via above the switch and routing enamel-wire from capacitor of switch to 3V3-Source
    - BB is booting!
- current-readout is very noisy
    - add 470 nF over shunt, to get 570 nF -> much better, Lowpass changes from 796 kHz to 140 kHz
        - this cap is bad idea!
    - 2 V rising stable in 6 us, falling in 10 - 16 us
    - add 1 nF over feedback-cap, to get 2 nF -> no Large Effect
    - TODO: switch back to small feedback loop without switch?
- GPIO-Edges -> BB - 1 k - 10 k PU, [33 R PRU] - LSF - 1 k - 10 k PU, Switch - TA
    - baseline test
        - BB-Source Low takes 50 ns from 3.3 to 0 V
        - TB-Receiv Low takes 2-3 us from 2 to 0.8 V
        - PRU-Recv  Low take 300 ns from 3.3 to 0 V
        - BB-Source Hi takes 100 ns to 3.3 V (100%)
        - TB-Receiv Hi takes 20 us from 0.8 to 2 V
        - PRU-Recv  Hi takes 800 ns from 0 to 3.3 V
    - -> try 2x 300 R Series Resistance, @5V only slightly above (8.3mA) current-limit of BB-Pins
        - 330 R || 1k = 248 R, 430 || 1k = 301 R
        - BB-Source Low 60 ns, High 80 ns
        - TB-Recv   low 1 us, Hi ~ 20 us
        - PRU_Rec   low 100 ns + 700 ns, Hi 400 ns
        - signal on target side between seriesRes and Switch is similar to target-output
        - signal on sys side between seriesRes and LSF is slower (400 ns rise instead of 50)
        - RefA = 0.961 V, RefB = 1.526 V -> fet-diode = 565 mV
    - lower RefB Resistor from 240k to 200k
        - TB-Recv   low 1-1.5 us, high 15-20 us
        - RefA = 1.053 V, RefB = 1.611 V -> fet-diode 558 mV
    - PU on both sides lowered from 10k to 2.1k, (= 2.7k || 10k)
        - TB-Recv   low ~< 1 us, Hi 3-5 us
    - other ideas?
        - lower PU on both sides at least for uart & programming -> 2.1 k seem to do the trick
        - capacity of line?
        - remove sys-series-resistor
        - disconnect pru-side
- WD is not starting the BB -> Pulse too short

TODO: look for voltage-spikes on coils when turning off power

Mods for HWv2.2
-----------------

- analog switch to pru
    - drill out via with <1mm drill, first layer is enough, trace from IC to Cap should stay intact
    - route wire from cap, through mounting hole to P9-2/3 (3V3 of BB)
- fast gpio-lines for swd and uart with stronger PUs, and lower series resistance
    - target side: on lower LSF (U12),
        - 10 k PU-Array, add 2.7k in parallel to lower 4 resistors, results in ~2.1 k
        - 1 k SeriesResistor-Array, add 100 R in parallel to lower 4 resistors, results in 91 Ohm
    - sys side:
        - same treatment for PUs, above P9-16, above / between P9-18/20, above left side P9-24, above right side P9-26
        - 1 k Series-Array, add 430 R in parallel
    - LSF - 1M parallel to existing 240 k on RefB -> resulting 200 k
- stabilize current measurement
    - 22 pF to GND on amplified path, right before ADC -> 22+5 pF + 100 k -> 60 kHz
    - additional 1 nF Cap on Feedback LP, both paths
    - Terminate unused Ports with 1 uF
    - remove 100 nF parallel to shunt
- stabilize IO-Buf-Voltage
    - cut left trace between 10 R and 1 nF, add 1k

- summary: 22 additional 0402-parts, 1 removed 0402, 2 cuts, 1 enamel trace -> ~ 1 h manual work

Mod v2.2 close the gap to v2.4
-------------------------------

- mostly emulator related, due to 10 already produced PCBs
- boost converter - raise voltage to >6V - R104 from 576k to 680k
- Emu
    - DAC-lowpass 1nF on TP3, after R5, same on TP2
    - ADC-Lowpass R10 100k to 33R, add 10 nF after that (on TP4)
    - Shunt-smoothing, C6 100nF to 10nF
- general improvement
    - switch enamel wire from 3v3 to 5vIn for analog switch that guards the boot-pins
    - extra kapton tape for enamel wire around mounting hole (possible easy short)

- EMU: try removing C3 1nF for more stable OpAmp-FB -> bad idea
    - C3 200 pF
    - C3 1 nF -> OK
    - R8 5k1 -> OK, but should be lower
    - R8 10k
    - R1 5k1 -> fine
    -> final change: C3 stays 1nF, R8 & R1 now 5k1
- remove most of the coils
    - 10V -> L13
    - -6V -> L11
    - A5V -> L7
- EMU increase shunt from 2R to 10 R (R9) and RGain R12 from 210R to 1.1k
    - lower noise, specially for low currents

- profiling shows:
    - 10k Feedback:
        - 0 mA load, 30 mVpp oscillation with 400 kHz
        - 40 mA load, 12 mVpp, no oscillation
        - 40 mA loadswitch, 320 mVpp drop for 40 us
    - 5k1 Feedback:
        - 0 mA load, 26 mVpp oscillation with 400 kHz
        - 40 mA load, 12 mVpp, no oscillation
        - 40 mA loadswitch < 200 mVpp drop for 25 us
    - 5V out @ 50 mA reduces Voltage to 4.27 V
        - 100 mV comes from 2 R Shunt
        - 20 mV come from trace after feedback-loop
        - remaining drop is due to 5V supply

Profiling 2R Shunt::

    SMU-reference: 1.000 mA @ 3.1999 V;   emu-c-raw: mean=5000.10, stddev=3.30 @ 3.200 V
    SMU-reference: 5.000 mA @ 3.1998 V;   emu-c-raw: mean=24741.11, stddev=19.33 @ 3.200 V
    SMU-reference: 10.000 mA @ 3.1997 V;   emu-c-raw: mean=49409.33, stddev=19.37 @ 3.200 V
    SMU-reference: 15.000 mA @ 3.1996 V;   emu-c-raw: mean=74101.05, stddev=37.38 @ 3.200 V
    SMU-reference: 20.000 mA @ 3.1995 V;   emu-c-raw: mean=98767.96, stddev=37.42 @ 3.200 V
    SMU-reference: 25.000 mA @ 3.1994 V;   emu-c-raw: mean=123441.02, stddev=36.68 @ 3.200 V
    SMU-reference: 30.000 mA @ 3.1993 V;   emu-c-raw: mean=148106.87, stddev=37.72 @ 3.200 V
    SMU-reference: 35.000 mA @ 3.1991 V;   emu-c-raw: mean=172779.27, stddev=42.50 @ 3.200 V
    SMU-reference: 40.000 mA @ 3.1990 V;   emu-c-raw: mean=197441.15, stddev=42.80 @ 3.200 V
    SMU-reference: 45.000 mA @ 3.1953 V;   emu-c-raw: mean=222110.22, stddev=41.39 @ 3.200 V
    SMU-reference: 50.000 mA @ 3.1811 V;   emu-c-raw: mean=246769.44, stddev=40.81 @ 3.200 V

    SMU-reference: 1.000 mA @ 4.3999 V;   emu-c-raw: mean=4999.34, stddev=3.33 @ 4.400 V
    SMU-reference: 5.000 mA @ 4.3998 V;   emu-c-raw: mean=24741.03, stddev=19.48 @ 4.400 V
    SMU-reference: 10.000 mA @ 4.3997 V;   emu-c-raw: mean=49407.86, stddev=19.54 @ 4.400 V
    SMU-reference: 15.000 mA @ 4.3995 V;   emu-c-raw: mean=74099.36, stddev=37.22 @ 4.400 V
    SMU-reference: 20.000 mA @ 4.3994 V;   emu-c-raw: mean=98767.49, stddev=37.35 @ 4.400 V
    SMU-reference: 25.000 mA @ 4.3993 V;   emu-c-raw: mean=123442.35, stddev=36.73 @ 4.400 V
    SMU-reference: 30.000 mA @ 4.3992 V;   emu-c-raw: mean=148108.01, stddev=37.72 @ 4.400 V
    SMU-reference: 35.000 mA @ 4.3863 V;   emu-c-raw: mean=172779.94, stddev=39.42 @ 4.400 V
    SMU-reference: 40.000 mA @ 4.3481 V;   emu-c-raw: mean=197442.74, stddev=38.15 @ 4.400 V
    SMU-reference: 45.000 mA @ 4.2972 V;   emu-c-raw: mean=222114.24, stddev=36.88 @ 4.400 V
    SMU-reference: 50.000 mA @ 4.2273 V;   emu-c-raw: mean=246772.54, stddev=34.40 @ 4.400 V

    SMU-reference: 1.000 mA @ 4.9694 V;   emu-c-raw: mean=4998.55, stddev=3.10 @ 5.000 V
    SMU-reference: 5.000 mA @ 4.9209 V;   emu-c-raw: mean=24741.21, stddev=17.52 @ 5.000 V
    SMU-reference: 10.000 mA @ 4.8602 V;   emu-c-raw: mean=49408.38, stddev=17.40 @ 5.000 V
    SMU-reference: 15.000 mA @ 4.7982 V;   emu-c-raw: mean=74101.53, stddev=32.35 @ 5.000 V
    SMU-reference: 20.000 mA @ 4.7337 V;   emu-c-raw: mean=98768.89, stddev=32.09 @ 5.000 V
    SMU-reference: 25.000 mA @ 4.6663 V;   emu-c-raw: mean=123444.18, stddev=31.66 @ 5.000 V
    SMU-reference: 30.000 mA @ 4.5959 V;   emu-c-raw: mean=148110.96, stddev=32.14 @ 5.000 V
    SMU-reference: 35.000 mA @ 4.5221 V;   emu-c-raw: mean=172783.01, stddev=34.65 @ 5.000 V
    SMU-reference: 40.000 mA @ 4.4440 V;   emu-c-raw: mean=197444.95, stddev=34.46 @ 5.000 V
    SMU-reference: 45.000 mA @ 4.3607 V;   emu-c-raw: mean=222116.58, stddev=34.18 @ 5.000 V
    SMU-reference: 50.000 mA @ 4.2701 V;   emu-c-raw: mean=246776.35, stddev=33.46 @ 5.000 V

Profiling 10R Shunt::

    SMU-reference: 1.000 mA @ 3.2001 V;   emu-c-raw: mean=5130.99, stddev=3.16 @ 3.200 V
    SMU-reference: 5.000 mA @ 3.2001 V;   emu-c-raw: mean=25605.70, stddev=21.25 @ 3.200 V
    SMU-reference: 10.000 mA @ 3.1999 V;   emu-c-raw: mean=51186.94, stddev=21.20 @ 3.200 V
    SMU-reference: 15.000 mA @ 3.1998 V;   emu-c-raw: mean=76793.88, stddev=40.36 @ 3.200 V
    SMU-reference: 20.000 mA @ 3.1996 V;   emu-c-raw: mean=102374.39, stddev=40.14 @ 3.200 V
    SMU-reference: 25.000 mA @ 3.1995 V;   emu-c-raw: mean=127962.74, stddev=39.88 @ 3.200 V
    SMU-reference: 30.000 mA @ 3.1993 V;   emu-c-raw: mean=153542.74, stddev=40.43 @ 3.200 V
    SMU-reference: 35.000 mA @ 3.1992 V;   emu-c-raw: mean=179127.57, stddev=46.09 @ 3.200 V
    SMU-reference: 40.000 mA @ 3.1991 V;   emu-c-raw: mean=204702.33, stddev=45.85 @ 3.200 V
    SMU-reference: 45.000 mA @ 3.1938 V;   emu-c-raw: mean=230285.98, stddev=44.23 @ 3.200 V
    SMU-reference: 50.000 mA @ 3.1780 V;   emu-c-raw: mean=255859.07, stddev=43.50 @ 3.200 V

    SMU-reference: 1.000 mA @ 4.4002 V;   emu-c-raw: mean=5130.41, stddev=3.24 @ 4.400 V
    SMU-reference: 5.000 mA @ 4.4001 V;   emu-c-raw: mean=25605.84, stddev=21.32 @ 4.400 V
    SMU-reference: 10.000 mA @ 4.3999 V;   emu-c-raw: mean=51186.59, stddev=21.36 @ 4.400 V
    SMU-reference: 15.000 mA @ 4.3998 V;   emu-c-raw: mean=76798.10, stddev=40.39 @ 4.400 V
    SMU-reference: 20.000 mA @ 4.3996 V;   emu-c-raw: mean=102378.49, stddev=39.93 @ 4.400 V
    SMU-reference: 25.000 mA @ 4.3898 V;   emu-c-raw: mean=127967.95, stddev=34.89 @ 4.400 V
    SMU-reference: 30.000 mA @ 4.3194 V;   emu-c-raw: mean=153545.53, stddev=32.60 @ 4.400 V
    SMU-reference: 35.000 mA @ 4.2228 V;   emu-c-raw: mean=179133.17, stddev=33.42 @ 4.400 V
    SMU-reference: 40.000 mA @ 4.1050 V;   emu-c-raw: mean=204707.56, stddev=32.38 @ 4.400 V
    SMU-reference: 45.000 mA @ 3.9764 V;   emu-c-raw: mean=230292.51, stddev=31.78 @ 4.400 V
    SMU-reference: 50.000 mA @ 3.8379 V;   emu-c-raw: mean=255862.87, stddev=31.12 @ 4.400 V

    SMU-reference: 1.000 mA @ 4.9618 V;   emu-c-raw: mean=5129.80, stddev=2.93 @ 5.000 V
    SMU-reference: 5.000 mA @ 4.8830 V;   emu-c-raw: mean=25603.63, stddev=16.67 @ 5.000 V
    SMU-reference: 10.000 mA @ 4.7831 V;   emu-c-raw: mean=51188.07, stddev=16.38 @ 5.000 V
    SMU-reference: 15.000 mA @ 4.6804 V;   emu-c-raw: mean=76788.55, stddev=30.26 @ 5.000 V
    SMU-reference: 20.000 mA @ 4.5753 V;   emu-c-raw: mean=102370.88, stddev=30.14 @ 5.000 V
    SMU-reference: 25.000 mA @ 4.4677 V;   emu-c-raw: mean=127964.19, stddev=29.70 @ 5.000 V
    SMU-reference: 30.000 mA @ 4.3576 V;   emu-c-raw: mean=153546.69, stddev=29.32 @ 5.000 V
    SMU-reference: 35.000 mA @ 4.2441 V;   emu-c-raw: mean=179136.95, stddev=31.96 @ 5.000 V
    SMU-reference: 40.000 mA @ 4.1266 V;   emu-c-raw: mean=204716.23, stddev=31.68 @ 5.000 V
    SMU-reference: 45.000 mA @ 4.0034 V;   emu-c-raw: mean=230304.75, stddev=31.84 @ 5.000 V
    SMU-reference: 50.000 mA @ 3.8733 V;   emu-c-raw: mean=255879.39, stddev=31.02 @ 5.000 V

Boardchanges for v2.3
--------------------------

-> moved to TODO-Section

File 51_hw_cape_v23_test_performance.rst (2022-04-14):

Shepherd Cape v2.3 - Performance
================================

Tested
------

- WD is fine now -> Board gets turned on
- BB boots with Shepard Cape on
- BB-powered boot works, but turning Cape on crashes the 5V Rail (P9-7/8)
- WD restarting BB works

Troubleshooting
---------------

Profiling Ranges

- full range: 0 to 5V, 0 to 50 mA
- limited range: 1 to 3.9 V, 3uA to 40mA

Harvester - low current measurement-limit

- draining below 1-2 uA -> voltage seems to invert (SMU reports -0.3V), not caring about the set-voltage of the DAC
- adc-current values are equal to "zero"
- diode blocks (later tests show 2nA reverse current), because voltage at cathode (opAmp-Out) is similar high to DAC-Voltage
- something seems to reverse leak current -> tldr: it is the OPA189 Negative Input Pin
    - **OPA189 input** can leak max +-1 nA (input bias current) and differential input impedance is 100 MOhm (100nA to 10V)
    - AD8421 inputs can leak max 2x +-500 pA, tests show < 1 nA
    - OPA2388 input can leak max +-400 pA (spec), tests show < 1 nA
    - diode is rated for 40 nA but shows in tests 2 nA @ 5V (see picture below)
    - capacitor C34 (Opa-Feedback) could leak -> tests show < 1 nA @ +-5V-Range (see picture below)
    - and the op189 output -> not relevant due to safe diode and capacitor
    - removing R20 stops the leak -> hint at OPA189 or cap C34
    - removing C34 changes nothing -> final clue for OPA189
- that may never occur with a real harvesting source (or work as a hard-to-detect offset)
- baking pcb off (80 °C, 30min) had no effect (mentioned in datasheet)
- this leakage is often not existent when SMU is freshly started for the day -> firmware-update to 3.4.0 (2021-04, from 3.2.2 2016-04) did not help
    - see profile 25, whole voltage range, down to 0 uA
- changing R20 (Feedback-Lowpass) to 100R or 10k does not change behaviour
- tests with solar-cell (SM101K09L) shows that 2uA is near to dark environment
- old TODO:
    - reverse position of diode and shunt
    - OPA189 speaks of (8.3.3) input bias current clock feedthrough (switching input to correct intrinsic offset)
    - -> it seems to be the "zero-drift" feature of OPA189 that gets triggered wrongly
    - worst outcome: 1-2 uA offset in measurement
- Update: this problem went away by using another py-lib for the SMU (and cleaner, more explicit init)

Schematic of Harvester v2.3



Current Leakage for Capacitor 1nF (C0G)



Current Leakage for Harvest Port



Power from Solar Cell (SM101KO9L) in various conditions



Diode Comparison

- PMEG10010ELRX
    - rated for (extremely low leakage current) **4 nA @ 10 V & 25 °C** and 40 nA (typical, 150 nA max) at 100V & 25°C
    - measurement: -5 V result in **2.1 nA at room temperature**
    - seems the safest bet, because datasheet promises the spec
- SMMSD701T1G
    - rated for ~ 8-9 nA @ 6-12 V & 25 °C (curves in datasheet)
    - measurement: -5 V result in **1.4 nA at room temperature**
    - lowest leak-value but not distinguishable from PMEG-Version in Frontend
- RB168MM-40TR
    - rated for 50 (typical) to 550 uA reverse current @ 40 V
    - curves in datasheet show IR @ 5 V, 25°C at around 10 nA, up to 1000 nA at 75°C
    - measurement: -5 V result in **6.9 nA at room temperature**
- the first two diodes are fine!
- --> see media_v23/profiler_smu_diodes.csv

Reverse Current of Diodes



Harvester - Current Measurement

- 2R-Shunt, Gain x48 -> 10R Shunt, Gain x10
    - no significant effect from profiler
    - **keep synced to emulator to save parts**
    - **keep 2R-Shunt**
- Lowpass between InAmp and ADC
    - 100k results in high offset of > offset of 11'800 n for 0 nA (ADC input seems to be raised by ADC itself)
    - 1k results in offset = ~ 182 n (Good) and lower Noise, mostly on full range (3-14x better)
    - 100R seems to worsen limited area (slightly), but improve full range (almost x2)
    - Cap was varied to match 80 - 160 kHz lowpass, but influence is minimal
    - 0R caused trouble with voltage dependend current reading +-10uA from 0 to 5V
    - **33R / 10nF** is fine, limited range gets minimal worse, but full range improves
- buffered shunt (parallel cap C35)
    - 470 nF instead of nothing: 10 - 20% improvement on limited and full range
    - nothing instead of 100 nF: 5-10 % worse on full range, minimal better on limited range (but with 100 nF seems the better bet)
    - 100nF instead of nothing: ~10% improvement on both ranges
    - **later tuning showed almost no influence of the cap (0, 10, 100nF) only max_error gets limited in profiler**
    - **10nF does suffice!**
- buffered inputs (Caps on V_HRV and V_Sense)
    - adding 2x 100nF is ~ 10 % worse
    - **remove**
- different diode (try alternatives)
    - no significant effect between new (and better) SMMSD701T1G-Diode and (current) PMEG10010ELRX
- slower OpAmp-Feedback
    - R20, 10k instead of 1k or 100R: 10-12% improvement for both ranges, but only static case (lowpass 16 kHz)
    - later tuning showed that 100R (compared to 330, 1k) are preferred, because OpAmp has to be fast (for the nonlinearitiy, ie. in voltage sweeps
    - **faste OpAMp** is better, as long as stable
- DAC to OpAmp Connection
    - slower response helps measurement
    - current 1k & 1nF are fine -> 9 us risetime from rail to rail (same with 200R, 1nF)
    - 100R & 10nF seem to perform a bit better
- shield
    - is not hurting the measurement, but helps with noisy environments
- set DAC-Ref-voltage to external A5V
    - current-reading improvement, while voltage worsened? but error stayed after reversing the change
    - TODO: investigate

Harvester - Voltage Measurement

- bigger shunt Resistor is 5-10% worse
- C35 parallel to shunt is better than no Cap, 100 nF is fine, 10nF also
- R16 before ADC-V is better smaller, but filtering is also
- Cap before ADC-V is better, 10nF compared to nothing brings 10 % improvement
- R18 before OpAmp was 1k, removal brings 10 % improvement
- Caps 100nF on Pinheader-Inputs is 5-10 % worsening
- R20 low -> Voltage-Matcher should be rather fast (better for V_meas, worse for C_meas)
- DAC-Lowpass is fine, lower Freq helps measurement

Without ShuntBuffer the current reading may be noisy (1k OpAmp Feedback, 0nF Shunt-Buffer)



Improvement with 10nF ShuntBuffer



OpAmp is stable enough to lower FB to 100R -> this gets rid of the nonlinearity in the sweep (area where open circuit voltage meets voltage ramp):



Emulator

- can't produce 5 V with 50 mA
- even at 0 mA the limit of 5 V is not completely on point,
- at 50 mA around 4 V are usable without large error
- -> seems to be fine for modern electronics
- 2 R Shunt resistor is responsible of 100 mV drop (50 mA)
- R10 from 100k changed to 0R -> offset still around 15.x, similar as with 33R in harvester
- 5V-Voltage regulator needs at least +1V Input -> raise 6v_Rail from 5.4V to 6.17V -> Emulator improves to 50mA @ ~4.28V
- Opa388 seems to be worse than the Opa189 -> switch to this one



BB-Powered Mode

- turning cape on when on BB-USB-Power crashes the system
- 5V_BB (P9-7/8) gets connected to 5V Line with inductor and large 1mF Cap
- most inductors show only minimal influence -> remove them
- more capacity on power-line is better (A5V is most significant), see traces below

No additional Buffering on A5V-Line



1mF Cap on A5V line - less noise!



Stabilize ADC-Readings (work through datasheet for more design guideline hints)

- ADC ADS8691
    - use X7R caps for V_in and ref-pins
    - low impedance sense-input
- InAmp AD8421
    - VS with 100nF + 10uF
    - RG with minimized capacitance
    - connection to ADC: 100R + 3nF
    - ref-voltage with OP1177, with 5k feedback, no C, 10 uF buffer for OpAmp Input
    - low impedance connections, input can be buffered
- OpAmp Opa189
    - same as Opa388
    - seems more stable than opa388, fb-cap can be omitted
- OpAmp Opa388
    - shield / isolate from air-currents and heat-sources
    - place 100nF directly to pwr-in and use groundplane
- DAC8562
    - AVdd with 100pF, 1nF, 100nF, 1uF
    - VRef-Buffer, higher capacitance raises noise floor?
    - internal reference is more noisy (1.4 to 3x less noise with perfect external ref) -> fail because voltage has huge error (current got more stable though)
- LDO LP2989
    - bypass cap 10nF C0G or NP0
    - provide VIn >= VOut + 1V
- Inverter LT3487
    - Thermal Pad (GND) low impedance, many vias
    - bypass with X7R
    - negative channel >= 10uF, pos Channel > 4.7 uF
    - phase lead caps for dampened load response (10-33pF parallel to FB-Res)
    - input can start at 1uF

Further noise-reducing Experiments:
- ADC: R10 33R, C62 10nF lowpass, 482kHz -> not much difference?
- R8, 5k OpAmp FB from 2k ->
    - 50 mV from std-dev 2800-4000-26, to 25-52-25
    - 2V from 31-60-31 to 25-56-30
- C3, 1nF OpAmp FB remove
    - 50mV completely unstable
- C5, remove 1uF DAC_Ref-Buffer
- DAC_Ref to A5V -> 1.4 to 3x less noise expected
    - 2V to std 22-55-29
    - current-channel is improving a bit overall (>5%), but with 20% larger max-errors
    - voltage-channel is 25-100% worse (mean)
- HRV
    - R20 back to 1k
    - R22 to 33 R, C140 to 10nF
    - R27 to 33 R, C36 to 10nF
    - R27 back to 100 -> 100R & 10 nF -> 160 kHz
    - R27 1k, C36 1nF -> same 160 kHz
    - C35 Buff, 0nF,  10nF, 100nF
    - R20 FB smaller 1k, 330R, 100R, 33R
        - 100R - 50 us for 0 to 5V, significantly smaller bump between ramp and open voltage
        - openC still 50us, even with reduced R27/200R -> Scope shows 9us risetime at diode (200R)
        - 1k (R27, back to normal) still 9us risetime on scope
- cross-supply DAC
- emu
    - DAC-out 33R, 10nF

Level-Translators

- speed for programming should exceed 1 MHz
- test shows safe flanks for ~ 200 kHz
- setup
    - Level translator: 74LVC2T45GS
    - Analog Switch: NLAS4684
- Risetimes for different configurations:
    - 1k + NLAS -> 1000 ns -> 434 pF tracecapacity calculated
    - 330R + NLAS -> 340 ns -> trace-capacity unchanged
    - 1k + removed 100k PU -> 1000 ns -> trace-capacity unchanged
    - 1k + removed NLAS -> **37 ns** -> 16 pF capacity, Trace ~20mm, w=0.2mm
    - 1k + removed NLAS + trace to PinHeader -> **45 ns** -> 19.5 pF (~40 mm Trace, w=0.2mm)
- capacitance
    - scope probe = 13 pF
    - Line-Capacitance = 1 pF / 7mm
    - NLAS-Capacitance = 414 pF -> both outputs behave a bit different ~ 10 % off
    - C_off = 104 pF (typical), NLAS-Datasheet @ 1 MHz
    - C_on = 330 pF (typical), NLAS-Datasheet @ 1 MHz
- Pin-Capacitance of uC, and drive capabilities
    - nRF52  3-4 pF, gpio current is 14/15 mA
    - msp430 5pF, gpio current is 6 mA
    - AM335x 5.5 pF, gpio current is 8 mA
- **constraints for the next analog switch**
    - VIn >= 5V
    - capacitance << 100 pF
    - leakage << 100 nA
    - https://www.mouser.de/c/semiconductors/switch-ics/analog-switch-ics/?mounting%20style=SMD%2FSMT&number%20of%20channels=2%20Channel~~7%20Channel&instock=y&rp=semiconductors%2Fswitch-ics%2Fanalog-switch-ics%7C~Number%20of%20Channels&sort=pricing
    - https://www.mouser.de/c/semiconductors/switch-ics/analog-switch-ics/?configuration=1%20x%203PDT~~1%20x%204PDT%7C~1%20x%20DPDT%7C~2%20x%20DPDT~~2%20x%20DPST%7C~2%20x%20SP4T~~2%20x%20SPDT%7C~3%20x%20DPDT~~3%20x%20SPDT%7C~4%20x%20SPDT%7C~6%20x%20DPDT~~8%20x%20SPDT&mounting%20style=SMD%2FSMT&instock=y&sort=pricing&rp=semiconductors%2Fswitch-ics%2Fanalog-switch-ics%7C~Configuration

Vc = Vs * (1 - e^(-t/(R*C)));
C = t * log(e)/(R*log(Vs/(Vs-Vc)));
tau = R*C;
fc = 1/(2*pi*R*C);

Close Contestants for SPDT (or DPST, naming is not precise), roughly ordered from cheap to expensive

- NLAS4684, 5.5V In, ~330 pF, 1-2 nA Leakage, < 1 Ohm -> perfect for analog voltage supply to targets
- FSA2258, 4.3V In (max 5.5V), ~ 50pF, 10 nA Leak -> using 5V is too risky
- DIO3712, 6V In, ~ 10pF, max 2 uA Leak -> typical leakage unknown, too risky
- **PI5A4158**, 5.5V In, ~ 34pF, 40 nA Leak -> strange package 1x3mm
- DIO1269, 5.5V In, ~ 120 pF, 20nA Leak
- DG2735A, 6V In, ~ 120pF, 10 nA Leak,
- NLAS3158, 5.5V In, 19 pF, 100nA Leak,
- DGQ2788, 6V in, 26pF, 1.2uA Leak,
- FSA2275, 6V in, ~ 25pA, 1uA Leak
- **PI5A100Q**, 4SPDT, <6V, 10 Ohm, 18 pF, 80nA max, 70pA typ !!!! (5x5mm QSOP16)

Contestants for SPST (>= 4x, one EN is fine), roughly ordered from cheap to expensive
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

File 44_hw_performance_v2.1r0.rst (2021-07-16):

HW Performance v2.1r0
=====================

Setup
-----

- BB powered by benchsupply 5.1 V, ~ 400 mA
- Shepherd powered by BB, VIn 5.08V
- Mods
    - big cap on input
    - switched rails for emu
    - later: lowpasses raised to 160 kHz
    - intermediate: rail B with short loop (exclude switch)
    - intermediate: small 100 nF Buffer Cap for Target 1 (instead of 1 uF)
    - later: 1 Ohm Shunt on Rail B, 100 Ohm for InAmp for 1:100 Amp
    - later: railB, long loop, 1.6 MHz Feedback Lowpass with 100 Ohms
- recorder
    - 1 kOhm from V_virtBuf to V_harvest
    - v_harvest connected to V_sense
- Emu
    - 1 kOhm on V_supply on target 1

- scope screenshots are in ./media_v2.1r0

Voltage Drop on Enable
----------------------
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

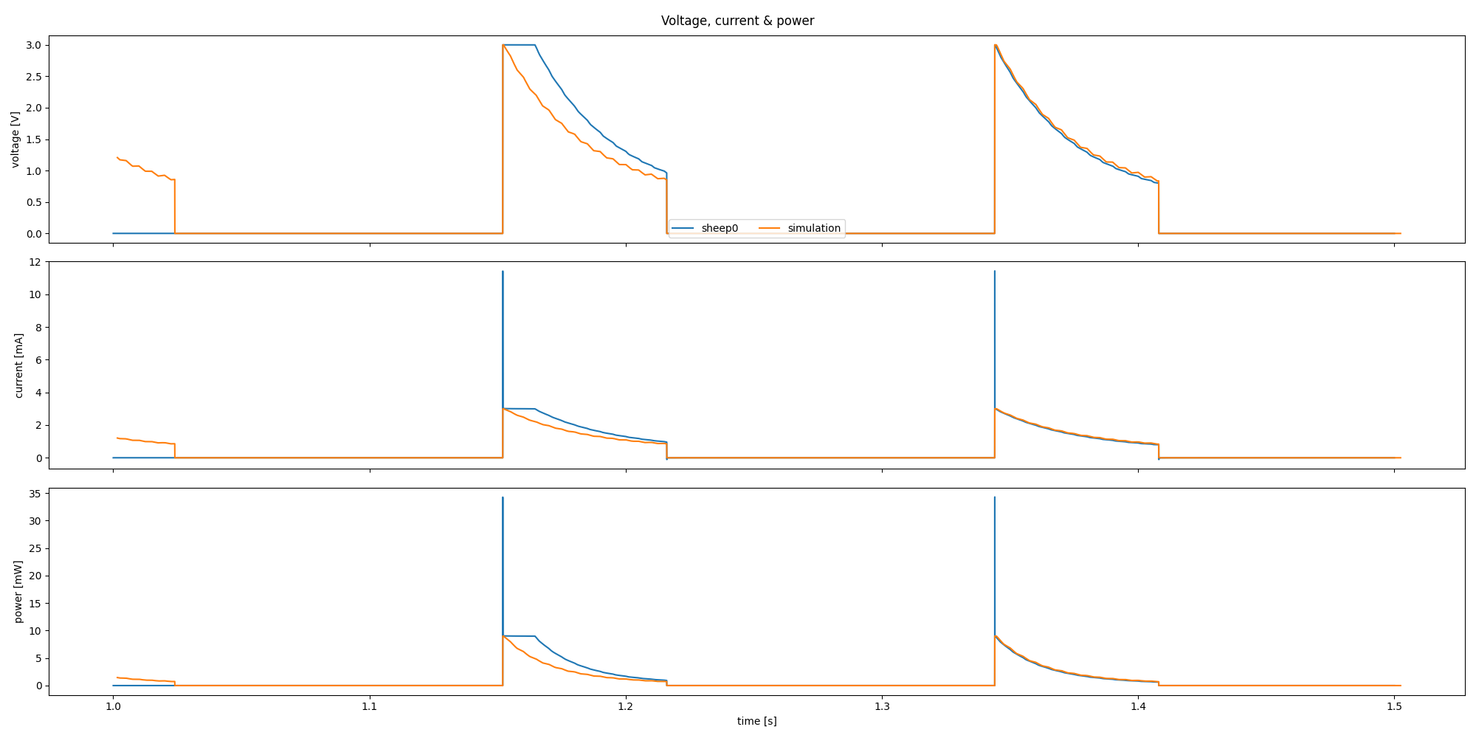
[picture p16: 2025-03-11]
docs/30_components_debugging/harvester_validation_v24/emu_ivcurve.multiplot_1s000_to_1s500.png

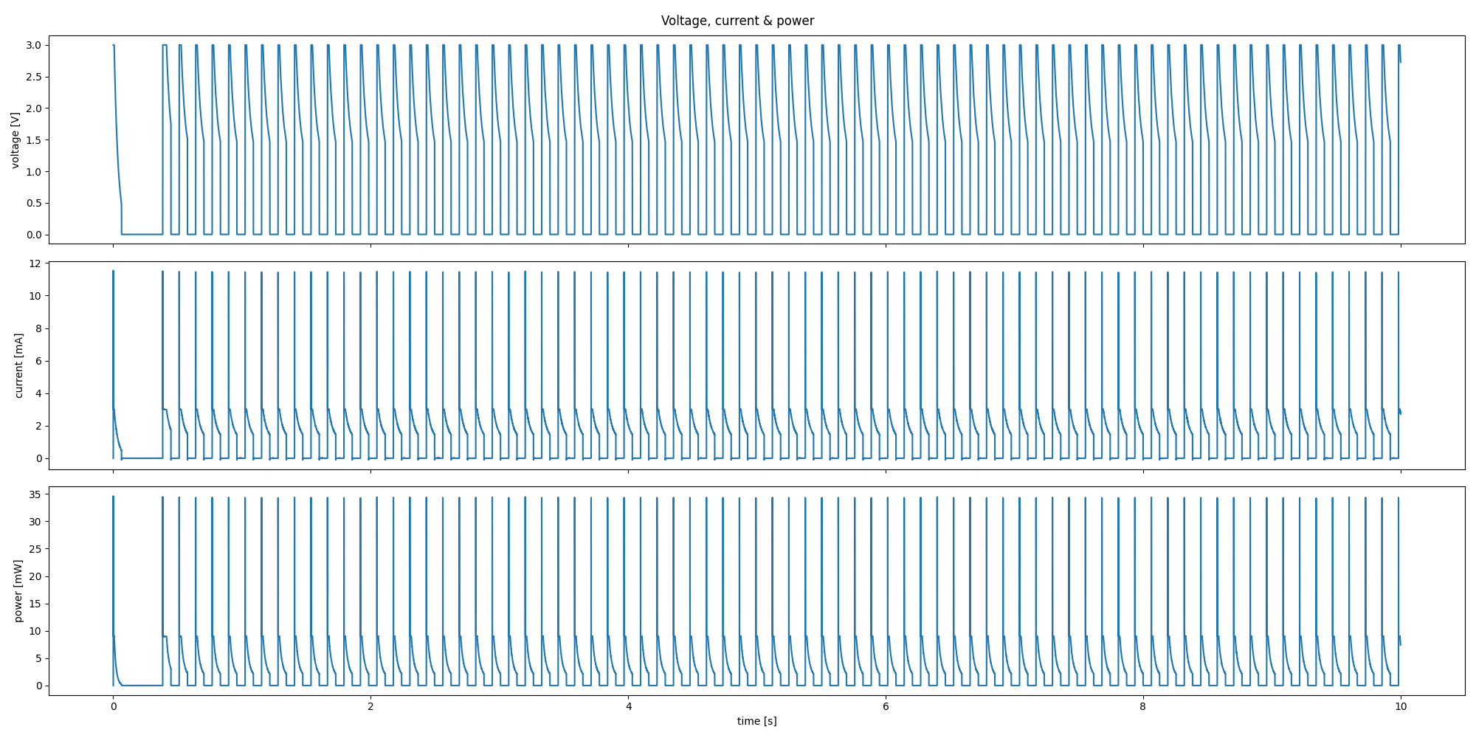
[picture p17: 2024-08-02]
docs/30_components_debugging/harvester_validation_v24/emu_opt.plot_0s000_to_10s000.png

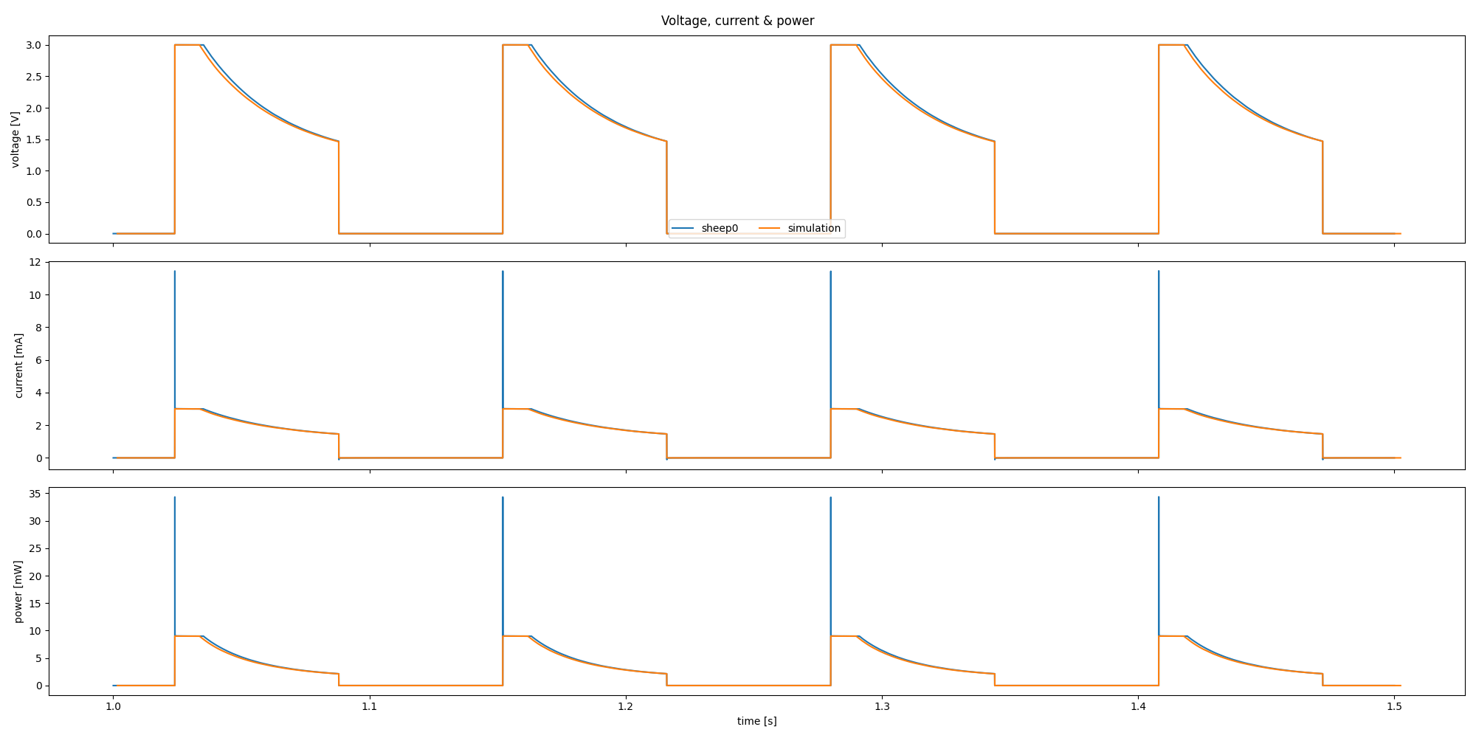
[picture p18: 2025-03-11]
docs/30_components_debugging/harvester_validation_v24/emu_opt.multiplot_1s000_to_1s500.png

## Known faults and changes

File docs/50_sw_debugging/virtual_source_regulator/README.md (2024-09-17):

# Virtual Source

## Current Features

- general features
    - fully customizable per yaml-parameter-set
    - or choose one of the predefined sets by name ie. "virtsource: BQ25504s" for the BQ-Regulator with pwr-good-schmitt-trigger
    - inherit from existing parameter-sets with ie. "converter-base: neutral" (neutral is default inheritance) ⇾ only altered parameters needed in new set
    - emulator can either record output or intermediate node (storage cap)
- Input
    - oneway, imagine a perfect diode at the start so no current can flow back
    - diode voltage-drop can be configured from 0 to x Volt
    - maxima for input voltage and current (power limit)
- Boost-converter, optional, with
    - enable minimum threshold voltage for input
    - disable maximum threshold for boost-output (intermediate voltage)
    - efficiency factor with 2D-LUT (12x12), depending on input voltage & current
        - thresholds are configurable in 2^n steps
        - voltage divisions are linear, depending on lowest threshold
        - current-divisions are log2, also depending on lowest threshold
        - example: voltage threshold n=7 is setting first array boundary to 2^7 = 128 uV, so lut[0] is for V < 128 uV, lut[1] is for 128 to 256 uV
- capacitor, optional, with
    - capacitance from 1 nF to 1 F
    - initial voltage
    - leakage current
    - switchable output, hysteresis with checks at defined intervals
    - power-good-signal with hysteresis either in intervals or immediate (schmitt-trigger)
- buck converter, optional, with
    - fixed output voltage
    - ldo-drop-voltage, alternatively working like a diode when buck is off or intermediate voltage is below output-voltage + drop-voltage
    - efficiency factor with 1D-LUT, depending on output-current
        - threshold is configurable in 2^n-steps
        - current-divisions are log2, depending on lowest threshold
        - example: current threshold n=5 is setting first array boundary to 2^5 = 32 nA, so lut[0] is for I < 32 nA, lut[1] is for [32, 64] nA, lut[2] is for [64, 128] nA
- switchable output
    - simulated external Capacitor - should be set to buffer size of target: fast transients can't be fully monitored by shepherd

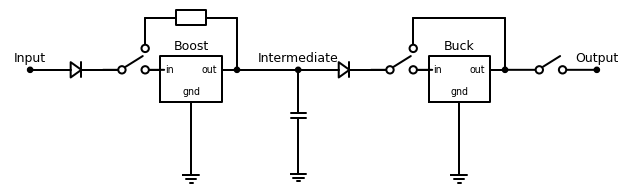
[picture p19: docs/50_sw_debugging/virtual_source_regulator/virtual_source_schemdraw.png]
vsrc


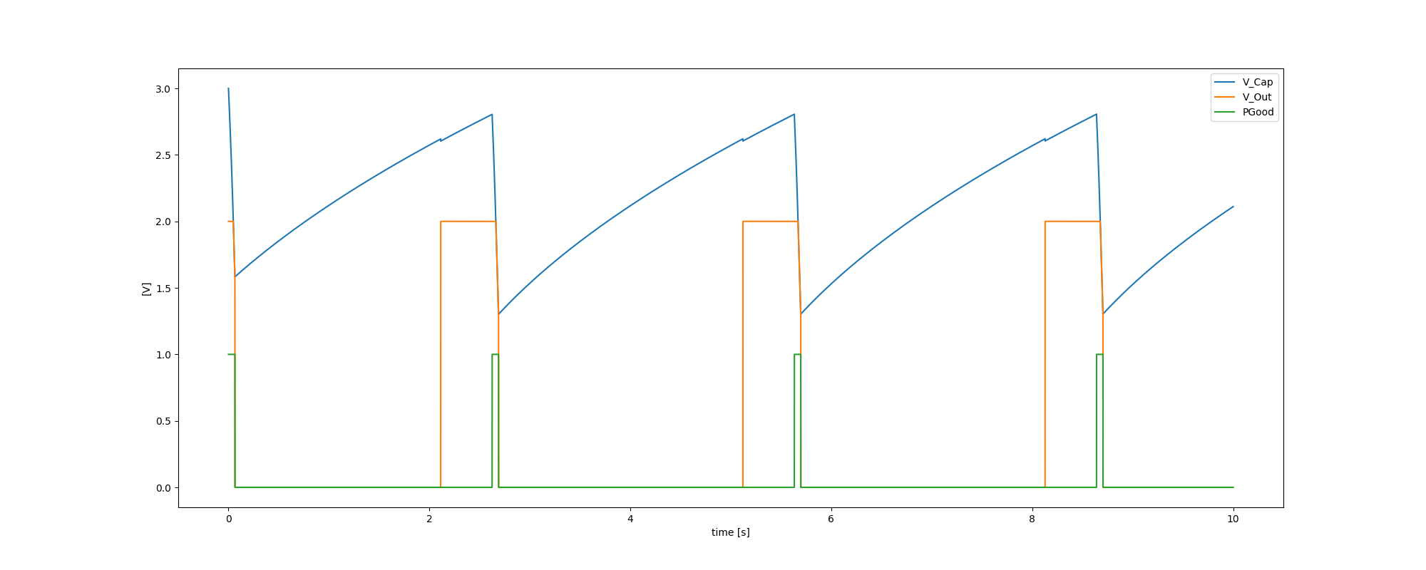
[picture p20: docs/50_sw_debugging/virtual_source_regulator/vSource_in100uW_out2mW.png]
Sim_i100uW_o2mW


## Implementation

- fixed point math with u32 & u64 with voltages in uV, currents in nA, power in fW, capacity in nF
- a python port is available
- modules
    - InputPower - calculated from recorded C-V-traces
    - OutputPower - voltage is set by DAC, current is measured by ADC
    - CapacitorUpdate - Voltage delta is calculated by resulting sum of Power
    - regulatorUpdate - handles internal States and Output
- limits
    - input power can be 56 bit in size (fW = uV * nA) ⇾ ~ 72 W
        - lowest value for algorithm is 64 fW, but due to ADC limitations 195 nA * 19 uV = 3.7 pW
    - output power can be 50 bit in size (fW = uV * nA) ⇾ ~ 1 W
        - difference to input due to inverted efficiency taking 14 instead of 8 bit
    - capacitor voltage can be 4.2 kV
        - due to custom faster division-function the range with low error is 0 to 5 V
        - optimization in calc_out_power limits voltage to 2^28 uV = 268 V, lower bound is 64 uV
    - storage capacitor can not be larger than 2.68 F (= 10*(2^28) nF), reasonable boundaries are [1 nF, 100 mF]
    -
- Speed in PRU (max timings)
    -   280 ns calc input power
    -  3200 ns calc output power
    - 10500 ns update capacitor
    -   470 ns update boost-buck
    - ~14000 ns for all (with space in between)
- Optimizing Algorithm for Speed
    - a custom uDiv() brings "update cap" down to 7500 ns, whole iteration takes 11684 ns
    - leaving out I_leakage is significantly faster (calc output is done in 310 ns instead of 3200, similar to input) but resulting output-power is wrong
        - seems to be undefined behavior introduced by implicit typecasting
        - ⇾ undefined it is! see documentation below
    - new ruleset:
        - u64 add, sub, shift are fine and fast!
        - u64 mul should be avoided, duration is depending on size of number (3000 - 4800 - 6400 ns for 4, 16, 32 bit)
        - u32 * u32 can give u64 result when both or last factor are typecasted - it is still fast! ⇾ uint64_t result = (uint64_t)num32a * (uint64_t)num32b;
- using the ruleset brings:
    -  280 ns calc input power
    -  430 ns calc output power
    - 5400 ns update capacitor
    -  540 ns update boost-buck
    - resulting time is around 6900 - 7060 ns
- using a custom mul64()-function
    -  280 ns calc input power
    -  500 ns calc output power
    -  950 ns update capacitor
    -  540 ns update boost-buck
    - resulting in < 2600 ns for all
- adding boundary checks for math-ops
    -  700 ns calc input power
    - 1350 ns calc output power
    - 1300 ns update capacitor
    -  580 ns update boost-buck
    - resulting in < 4300 ns for all
- TODO: benchmark new extended code

## How PRU0 Spends the 10 us per Cycle

- ~ 1 - 2 us busy waiting for trigger (headroom for more workload)
- 100 ns trigger ADC-Reading
- 200 ns getting to Sampling Routine
- 650 ns load remote buffer-values (input IV)
- 700 ns calculate input power
- 1100 ns read ADC, output current
- 1300 ns calculate output power
- 1300 ns update capacitor
- 580 ns update boost-buck
- 2000 ns write DAC (currently both channels are written for debug) and buffer-output
- 200 ns message handling

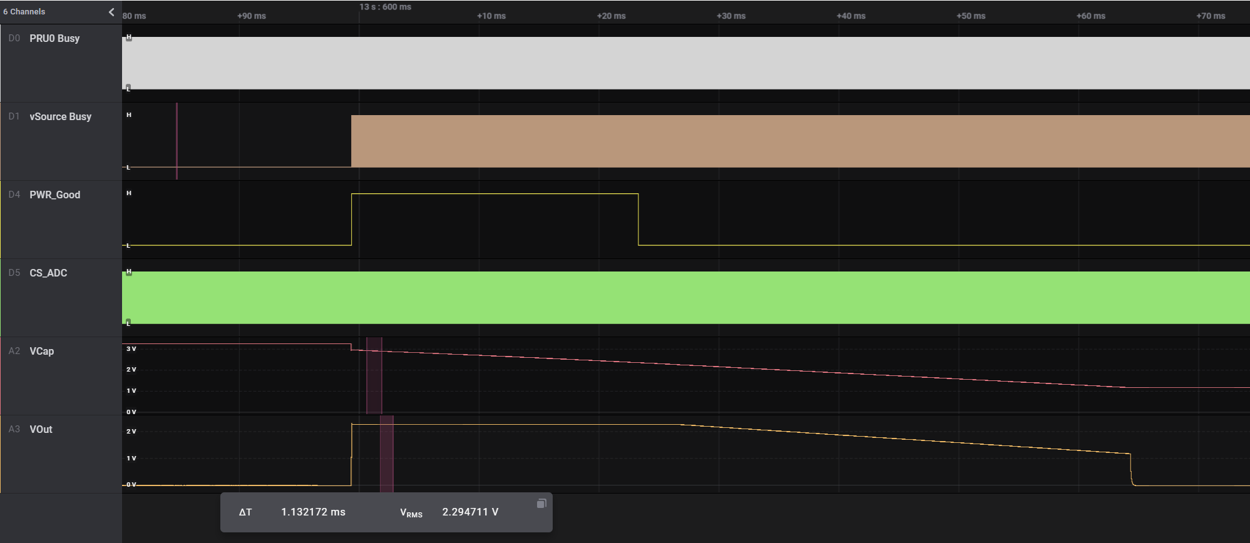
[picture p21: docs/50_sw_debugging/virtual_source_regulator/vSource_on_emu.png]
EmuSrc


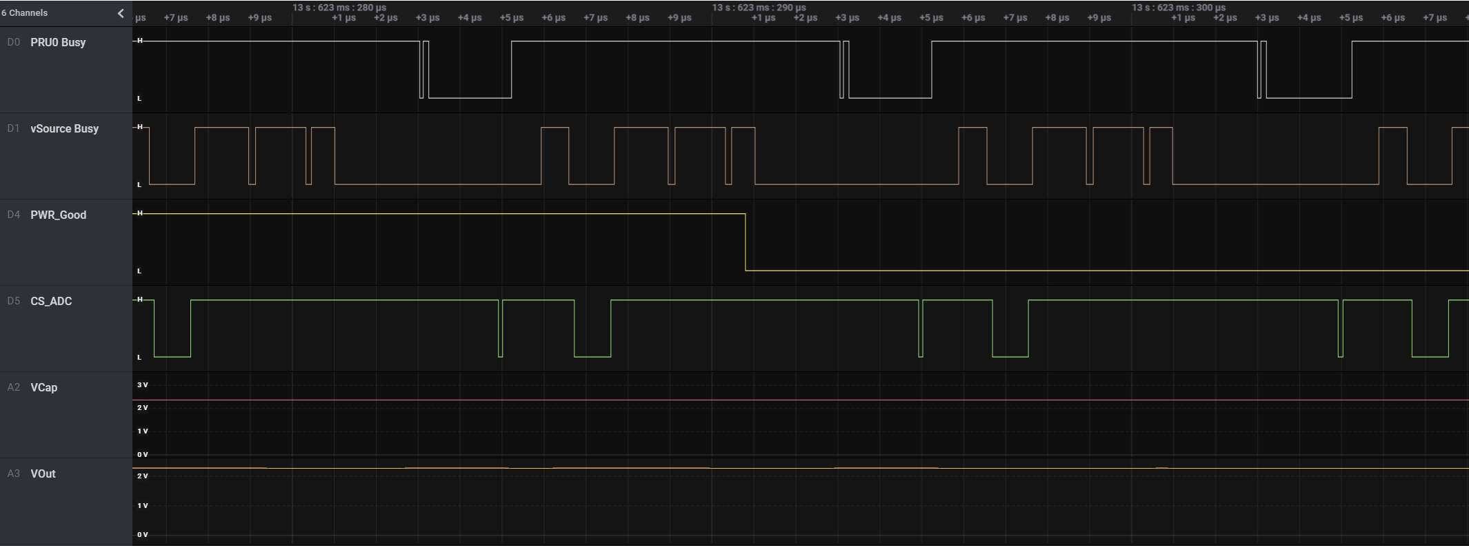
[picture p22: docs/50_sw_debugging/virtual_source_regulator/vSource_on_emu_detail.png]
EmuDetail


## Performance on real hardware

- dataset: indoor_solar/sheep4/office_sd.h5
- cap 22 uF, 50% eta_in, 80% eta_out
- sim-sets
    - 10 mA drain shows dutycycle of ~ 0.27 %, On-Time is ~ 800us
    - 1 mA drain, dutycycle ~ 2.7 %, On-Time ~ 8.16 ms.
- cap voltage moves between power-good-thresholds of 2.4 and 2.8 V

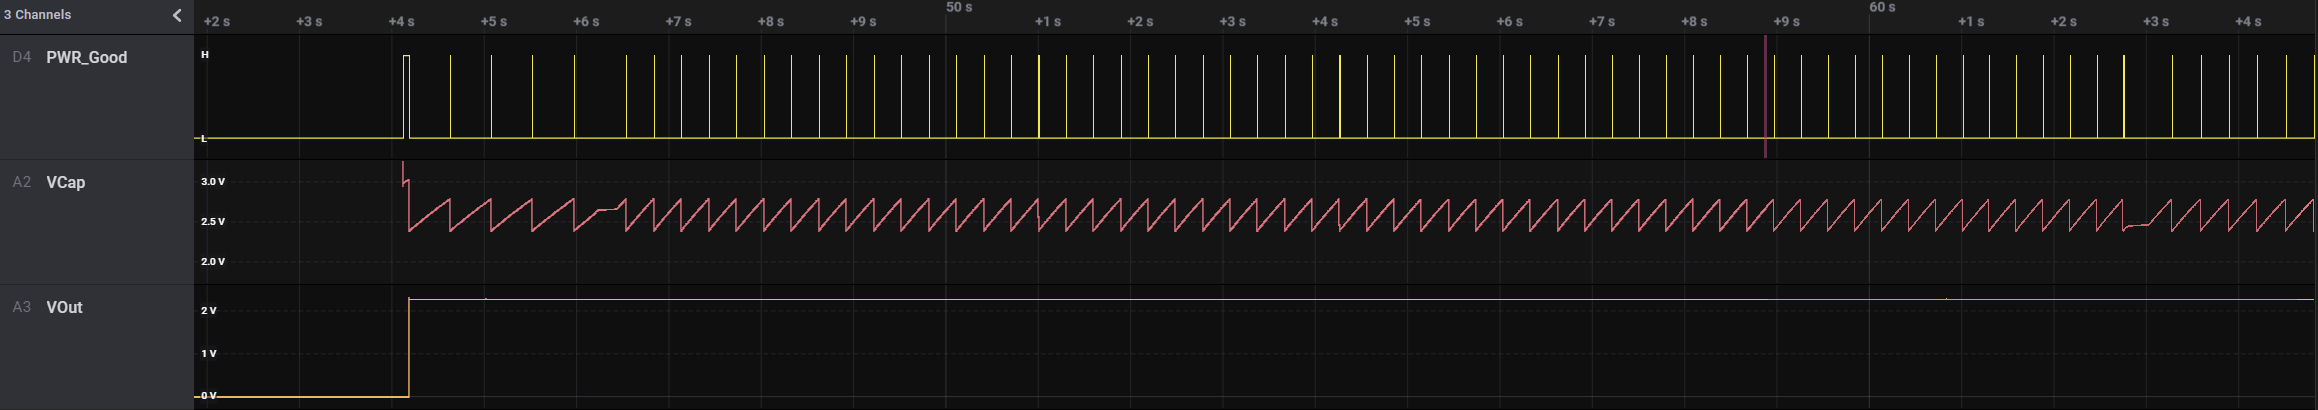
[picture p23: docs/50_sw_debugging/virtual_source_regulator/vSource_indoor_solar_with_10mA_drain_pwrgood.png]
vsrc_10mA


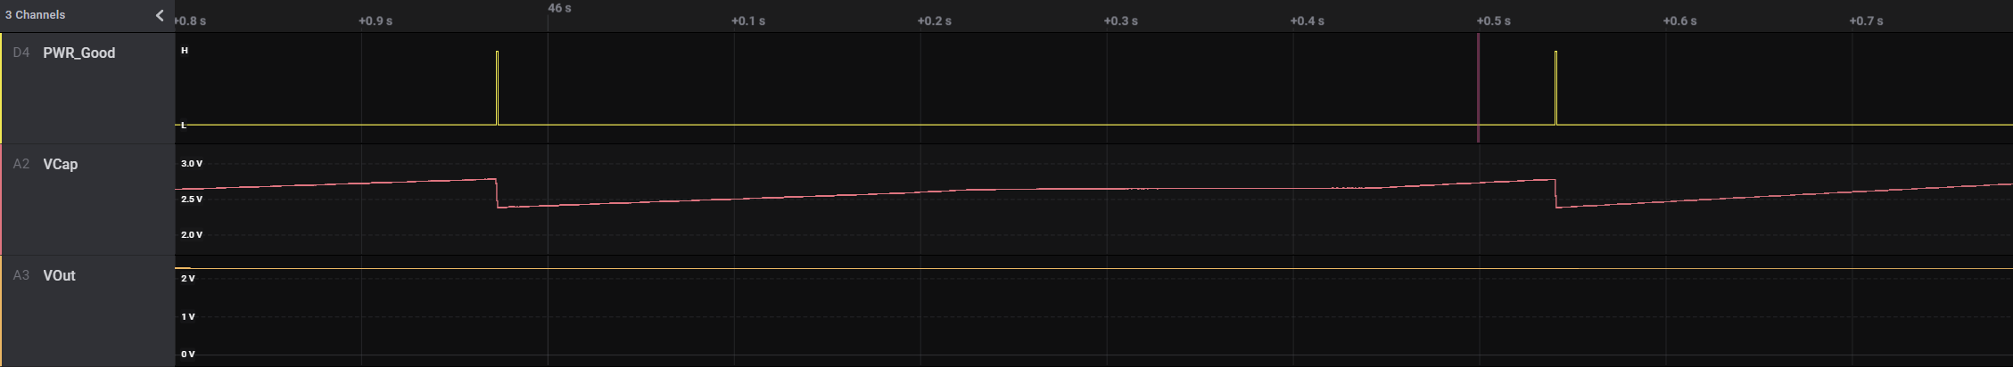
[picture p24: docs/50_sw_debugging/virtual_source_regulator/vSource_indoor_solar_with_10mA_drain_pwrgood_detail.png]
vsrc_10mA_detail


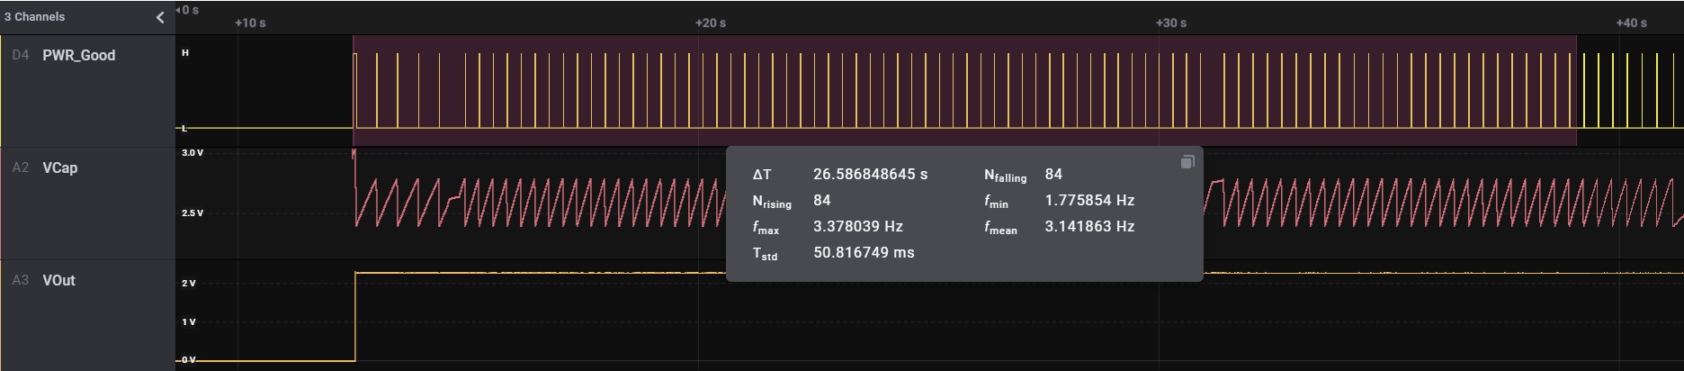
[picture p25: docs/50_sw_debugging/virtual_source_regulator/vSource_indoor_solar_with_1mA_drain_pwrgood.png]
vsrc_1mA


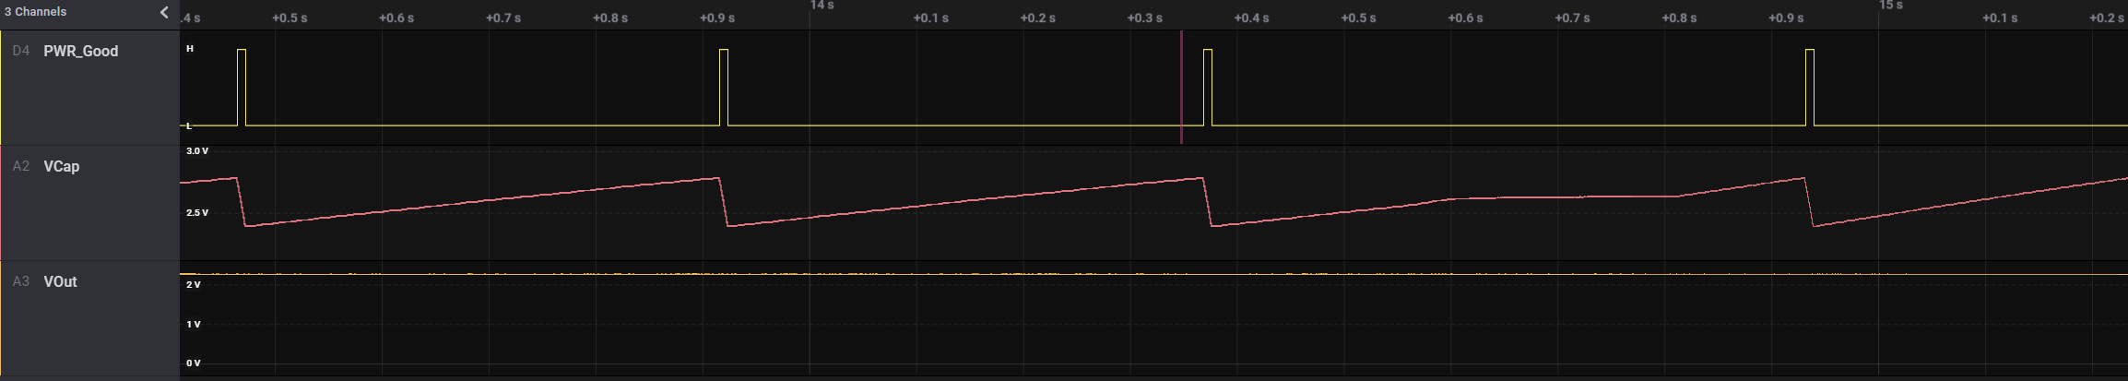
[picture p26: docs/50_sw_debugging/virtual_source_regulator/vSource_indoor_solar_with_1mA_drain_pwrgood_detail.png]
vsrc_1mA_detail


## Dev Scratch Area

TI Compiler behavior

```C
// u64 * u64 ⇾ 7 us
// u32 * u64 ⇾ 2.56 us
// u64 * u32 ⇾ 0.03 us, es rechnet nur u32*u32

uint64_t debug_math_fns(const uint32_t factor, const uint32_t mode)
{
    const uint64_t f2 = factor + ((uint64_t)(factor) << 32);
    const uint64_t f3 = factor - 10;
    GPIO_TOGGLE(DEBUG_PIN1_MASK);
    uint64_t result = 0;
    if (mode == 1)
    {
        const uint32_t r32 = factor * factor;
        result = r32;
    }									// ~ 28 ns, limits 0..65535
    else if (mode == 2)	result = factor * factor; 			// ~ 34 ns, limits 0..65535
    else if (mode == 3)	result = (uint64_t)factor * factor; 		// ~ 42 ns, limits 0..65535 ⇾ wrong behavior!!!
    else if (mode == 4)	result = factor * (uint64_t)factor; 		// ~ 48 ns, limits 0..(2^32-1) ⇾ works fine?
    else if (mode == 5)	result = (uint64_t)factor * (uint64_t)factor; 	// ~ 54 ns, limits 0..(2^32-1)
    else if (mode == 5)	result = ((uint64_t)factor)*((uint64_t)factor); // ~ 54 ns, limits 0..(2^32-1)
    else if (mode == 11)	result = factor * f2;				// ~ 3000 - 4800 - 6400 ns, limits 0..(2^32-1) ⇾ time depends on size (4, 16, 32 bit)
    else if (mode == 12)	result = f2 * factor;				// same as above
    else if (mode == 13)	result = f2*f2;					// same as above
    else if (mode == 21)	result = factor + f2;				// ~ 84 ns, limits 0..(2^31-1) or (2^63-1)
    else if (mode == 22)	result = f2 + factor;				// ~ 90 ns, limits 0..(2^31-1) or (2^63-1)
    else if (mode == 23)	result = f2 + f3;				// ~ 92 ns, limits 0..(2^31-1) or (2^63-1)
    else if (mode == 24)	result = f2 + 1111ull;				// ~ 102 ns, overflow at 2^32
    else if (mode == 25)	result = 1111ull + f2;				// ~ 110 ns, overflow at 2^32
    else if (mode == 26)	result = f2 + (uint64_t)1111u;			//
    else if (mode == 31)	result = factor - f3;				// ~ 100 ns, limits 0..(2^32-1)
    else if (mode == 32)	result = f2 - factor;				// ~ 104 ns, limits 0..(2^64-1)
    else if (mode == 33)	result = f2 - f3;				// same
    else if (mode == 41)	result = ((uint64_t)(factor) << 32u);		// ~ 128 ns, limit (2^32-1)
    else if (mode == 42)	result = (f2 >> 32u);				// ~ 128 ns, also works
    GPIO_TOGGLE(DEBUG_PIN1_MASK);
    return result;
}
```

## BQ25504 - Datasheet RevE

- Input MAX: 0.1 A, 3 V, 300 mW
- Input MIN: Cold Start Voltage 0.6 V, Harvesting down to 130 mV, Datasheet speaks of 10uW min Charging
- Quiescent Current Iq_vstor < 330 nA for UV Condition, 570 nA in OV
- Battery Charge Voltage 2.5 - 5.25 V
- VBAT_OK-Signal
- Caps
	- Input 4.23 - 5.17 uF
	- Storage 4.23 - 5.17 uF
	- Battery 100 uF and more
- VBatOV 2.5 - 5.25 V
- VBatUV 2.2 - VBatOV
- Input Efficiency (Page 9)
	- 10 uA: 0 % for 130 mV, 90 % for 3 V
	- 100 uA: 10 % for 130 mV, 90 % for 3 V
	- 10 mA: 40 % for 130 mV, 93 % for 3 V
	- model needs better definition of limits
- TODO: continue on p. 11, https://www.ti.com/lit/ds/symlink/bq25504.pdf?ts=1625558784652&ref_url=https%253A%252F%252Fwww.ti.com%252Fproduct%252FBQ25504%253Futm_source%253Dgoogle%2526utm_medium%253Dcpc%2526utm_campaign%253Dapp-null-null-GPN_EN-cpc-pf-google-eu%2526utm_content%253DBQ25504%2526ds_k%253DBQ25504%2526DCM%253Dyes%2526gclid%253DEAIaIQobChMI_6nZmf7N8QIVmrd3Ch3Q4AxNEAAYASAAEgKpwPD_BwE%2526gclsrc%253Daw.ds

### Implemented

- pru - check overflow with custom mul(), add(), sub() and limit to max / min
- add min to limits in python
- change efficiency to native 0 - 1 num
- extend converter: pre-power: voltage, duration
- extend converter: i-inp-max, v-inp-max,
- check and warn about limits in Python
- add BQ25504

### HowTo fill Efficiency LUTs:

- find lowest threshold for current and voltage
- it helps to add current/voltage-values for each column/row as comment on the outside
- additional help: use editor that can highlight a string and fill table with placeholders (1.00 or 0.00 should work)
- efficiency-graphs in datasheet allowed to deduct values and fill single columns and rows of 12x12-Table
- the bq25504-input LUT had less than 30 (of 144) undetermined values ⇾ interpolation with not much guesswork

## BQ25570

- implemented / defined and tested

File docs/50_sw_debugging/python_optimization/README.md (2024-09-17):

# Python Speed-Optimizations

## Benchmarking

Howto

```Shell
sudo python3 -m cProfile -o profile.pstats  /opt/shepherd/software/python-package/shepherd_sheep/cli.py -v run --config /etc/shepherd/example_config_emulation.yml
python -m pip install snakeviz
snakeviz.exe .\profile.pstats

sudo python3 -m cProfile -o profile.pstats  /opt/shepherd/software/python-package/shepherd_sheep/cli.py -v inventorize

# ⇾ cleaner call
sudo python3 -m cProfile -o profile.pstats /usr/bin/shepherd-sheep -v inventorize
```

PyCode-Performance

| Name                  | CPU-Load | Description                           |
|-----------------------|----------|---------------------------------------|
| h5-NoCompression      | 77 %     | 47 mb / 30s                           |
| h5-lzf                | 89 %     | 24 mb/ 30s                            |
| loggerOpt1 - ifVerb   | 84 %     | same                                  |
| loggerOpt2 - traceOff | 83 %     |                                       |
| profiler1             | 83 %     |                                       |
| with monitors         | 91 %     | tevent.wait() instead of time.sleep() |
| same w/o profiling    | 81 %     |                                       |

looking at individual commands - also imports

```Shell
sudo python3 -m timeit -n 1 -r 1 "import shepherd_core"
# 12.8 s on sheep, pydantic 2.4.0
# 11.5 s on sheep, pydantic 2.4.1
# 11.9 s on sheep, pydantic 2.4.2
# 12.4 s on sheep, pydantic 2.5.0 - new pydantic import-improvements?
# 12.1 s on sheep, pydantic 2.5.2
# 12.1 s on sheep, pydantic 2.6.1
# 12.8 s on sheep, pydantic 2.7.0 / 2.18.1 - with lib 24.4.2 (16.6s without cache, 17.7/13.8 deferred)
#  sudo rm /root/.cache/shepherd_datalib/fixtures.pickle
#
sudo python3 -X importtime -c "import shepherd_core"
# to shell
sudo python3 -X importtime -c 'from shepherd_core.data_models.task import EmulationTask' 2> profile_pydantic.csv
# to file, now only replace some symbols by ";" and open with excel to sort
```

In addition, there are benchmarks in the main-repo: https://github.com/orgua/shepherd/tree/main/software/python-package/tests_manual

## Optimization - Low-hanging Fruits

These things can be done to reduce cpu load:

- ditch lzf-compression for writing files
- compression-tradeoff: double the file-size for ~ 12 less percent-points cpu-load (absolut value)
- disable logging-sys-monitors (cpu/ram-usage, sync ... get written to h5-file) ⇾ per argument
- reduce python-logging ⇾ verbose level argument
- wait for python 3.11 and later ⇾ four performance-stages for cpython are planned (https://github.com/markshannon/faster-cpython/blob/master/plan.md)
- omit writing of timestamp
- overhaul buffer-exchange (segmented ring-buffer should go)
- [according to forum](https://forum.beagleboard.org/t/beaglebone-overclocking-success/11628) the CPU can be overclocked by 60%, RAM by 50%
    - sudo cpufreq-set -g powersave     ⇾ 230mA @ 300 MHz
    - sudo cpufreq-set -g performance   ⇾ 330mA @ 1 GHz
    - cpufreq-info

More Complex, but still easiest optimizations beyond that
- datastream from memory-carveout to hdf5-file should be ported to cython (seems to be possible)
- replace h5py by a more performant lib?
- "click" seems to be slowing down start of programs substantially (is it parsing the whole codebase?)

## Logging Performance-Impact

Logging-module of python has serious performance impact

- example: 4*10 msg/s in debug-mode are >20 % overhead on BB
- follow https://docs.python.org/3/howto/logging.html#optimization
- avoid assembling these 4 most critical fast-Strings
    - __init__.py/emulator.return_buffer(), external verbose
    - datalog.py/LogReader.read_buffers(), generator with internal verbose ⇾ good enough
    - shepherd_io.py/ShepherdIO.get_buffer(), external verbose
        - SharedMem.read_buffer(), external verbose & GPIO-Msg disabled
- try to avoid collection of useless data (thread,process,_srcfile)

Implemented Improvements:

- warn in config-yamls about impact of verbose>2
- avoid overhead (assembling strings, jump in logging-routines) by hiding verbose code in if-branch
- reduce or consolidate debug-code

## General python-Cleanups

- `range(len(x))` ⇾ `enumerate(x)`
- initializes `list([])` ⇾ `[]`, `dict()` ⇾ `{}`
- allow resizing the fifo-buffer, largest value seems to be 107 (< 10k pages)
- https://wiki.python.org/moin/PythonSpeed/PerformanceTips
- not needed `str()` casting for paths before open(), and a lot of other castings removed
- `asyncio.sleep()` or `threading.Event().wait()` in code? ⇾ use sleep(), .wait() has small overhead

- compile h5py for beagle ⇾ fails, see below
- cython, numba, nuitka, pypy: https://doc.pypy.org/en/latest/faq.html

## Updating Py-Libs (without compiling)

Watch out for H5Py improvements ⇾ main load according to profiler

Profiling-results for h5py-3.4

| runtime | Function                               |
|---------|----------------------------------------|
| 624 s   | total runtime                          |
| 26 s    | h5.shape                               |
| 96 s    | sleep                                  |
| 34 s    | h5.datalog.read_buffers.__getitem__    |
| 447 s   | h5.datalog.write_buffers               |
| 184 s   | h5.datalog.?.__getitem__(h5.group.py)  |
| 103 s   | h5.datalog.?._setitem__(h5.dataset.py) |

Update H5Py

```Shell
sudo /usr/bin/python3 -m pip show h5py
# ⇾ v2.1?
sudo /usr/bin/python3 -m pip list --outdated
sudo /usr/bin/python3 -m pip install --upgrade wheel h5py
# ⇾ v3.4
```

updated numpy is giving libblas-trouble

```Shell
sudo /usr/bin/python3 -m pip uninstall numpy scipy
sudo apt --reinstall install python3-numpy python3-scipy

# further update all packets
sudo /usr/bin/python3 -m pip install --upgrade click cryptography decorator distlib
# failing because of distutil greenlet: gevent platformdirs pybind11  msgpack-numpy
sudo /usr/bin/python3 -m pip install --upgrade pyyml six virtualenv zope.event zope.interface
# another distutils: xdg

sudo /usr/bin/python3 -m pip install --upgrade --force-reinstall h5py --no-binary :all:
# ⇾ still fails libhdf5.so after over 1h

# lib-experiments
sudo /usr/bin/python3 -m pip install --upgrade --force-reinstall h5py numpy scipy
sudo apt install python3-dev gfortran libopenblas-base liblapack3 libopenblas-dev liblapack-dev libatlas-base-dev
libopenblas* liblapack*
sudo apt remove libopenblas-base  # could be the culprit that overwrites the one working and needed lib
# https://stackoverflow.com/a/34956540
```

h5py-compilation-cookbook from kai (slightly modded):

```Shell
sudo apt-get install libhdf5-dev
sudo pip3 install --upgrade cython
ln -s /usr/include/locale.h /usr/include/xlocale.h
#sudo /usr/bin/python3 -m pip uninstall numpy h5py
#sudo /usr/bin/python3 -m pip install --only-binary=numpy numpy==1.17.5
sudo /usr/bin/python3 -m pip install --no-binary=h5py h5py
# ⇾ v3.4, created wheel filename=h5py-3.4.0-cp39-cp39-linux_armv7l.whl size=5487437
# ⇾ relatively quick, but no benefit to precompiled version
```

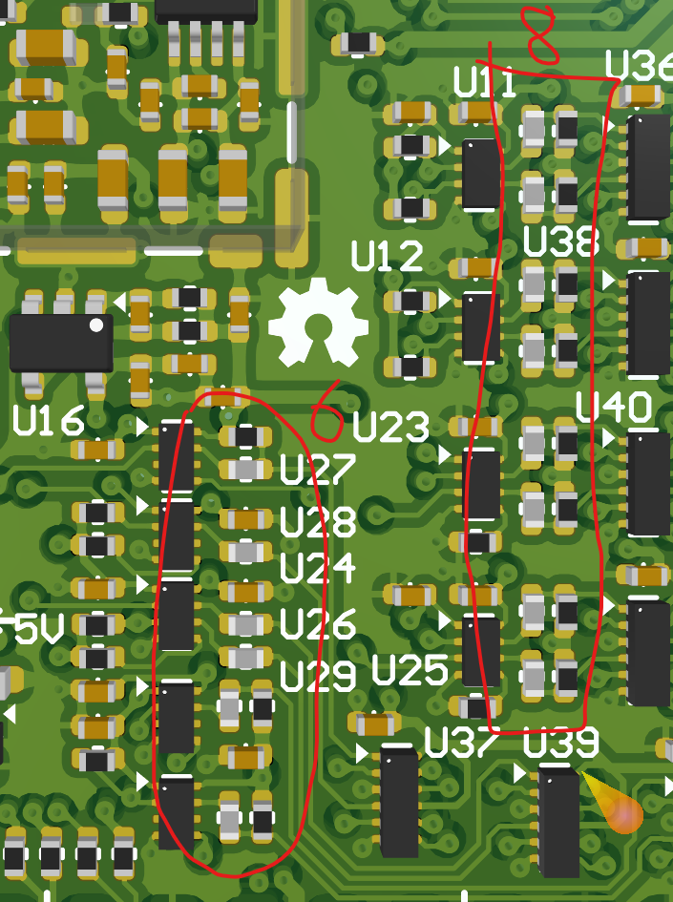
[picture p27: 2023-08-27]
docs/10_capes/media_v24/lvlTrans_resistor_changes.png

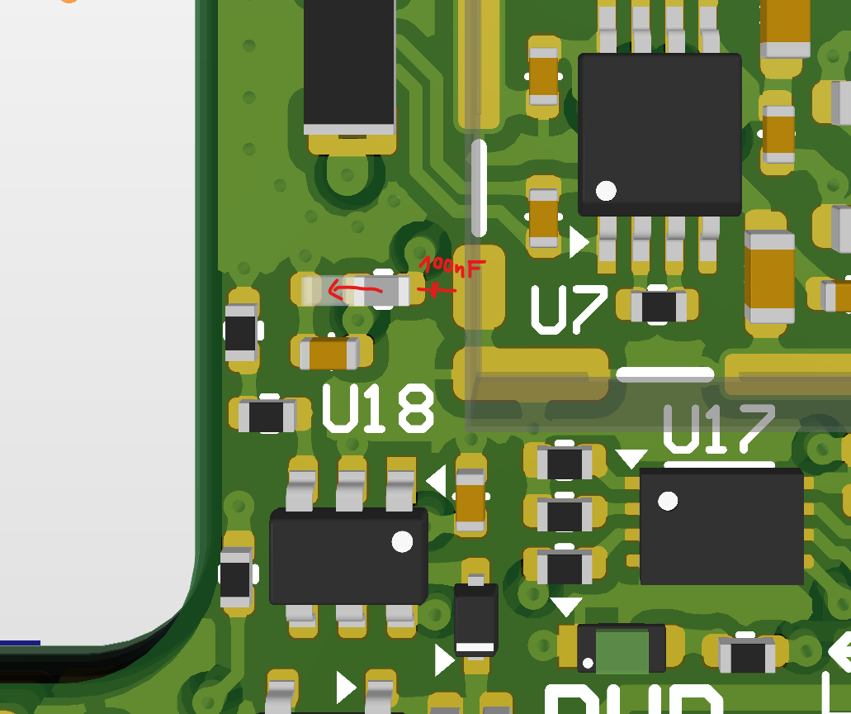
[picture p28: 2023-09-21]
docs/10_capes/media_v24/hrv_10mV_changes.png

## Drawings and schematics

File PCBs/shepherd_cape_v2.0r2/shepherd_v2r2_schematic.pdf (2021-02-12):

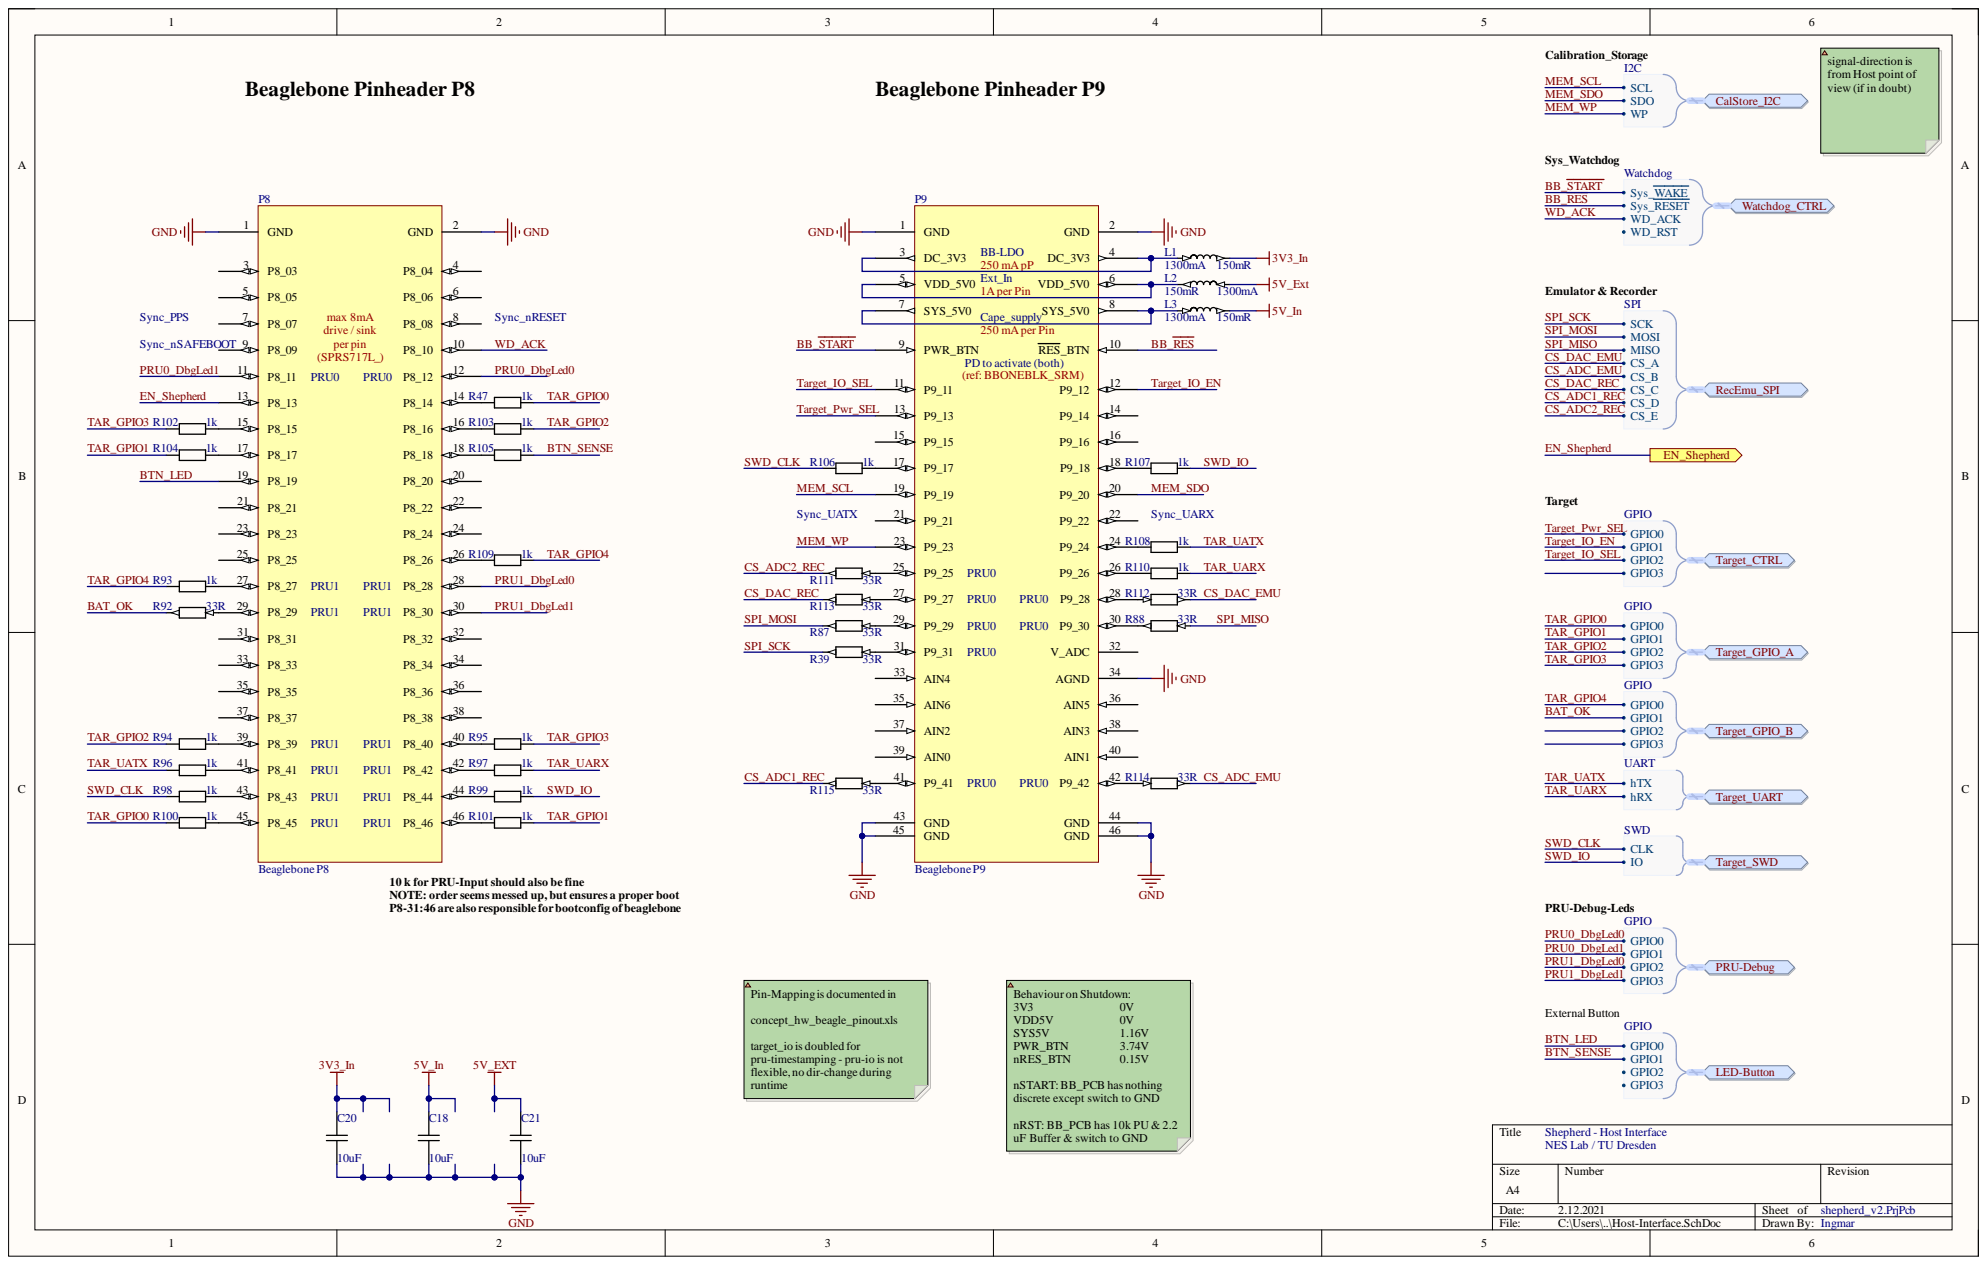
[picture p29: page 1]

signal-direction is
from Host point of
view (if in doubt)

PD to activate (both)
(ref: BBONEBLK_SRM)

10 k for PRU-Input should also be fine
NOTE: order seems messed up, but ensures a proper boot
P8-31:46 are also responsible forbootconfig of beaglebone

Pin-Mappingis documented in

target_io is doubled for
pru-timestamping - pru-io is not
flexible, no dir-change during
runtime

nSTART: BB_PCB has nothing
discrete except switch to GND

nRST: BB_PCB has 10k PU & 2.2
uF Buffer & switch to GND

Shepherd - Host Interface
NES Lab / TU Dresden

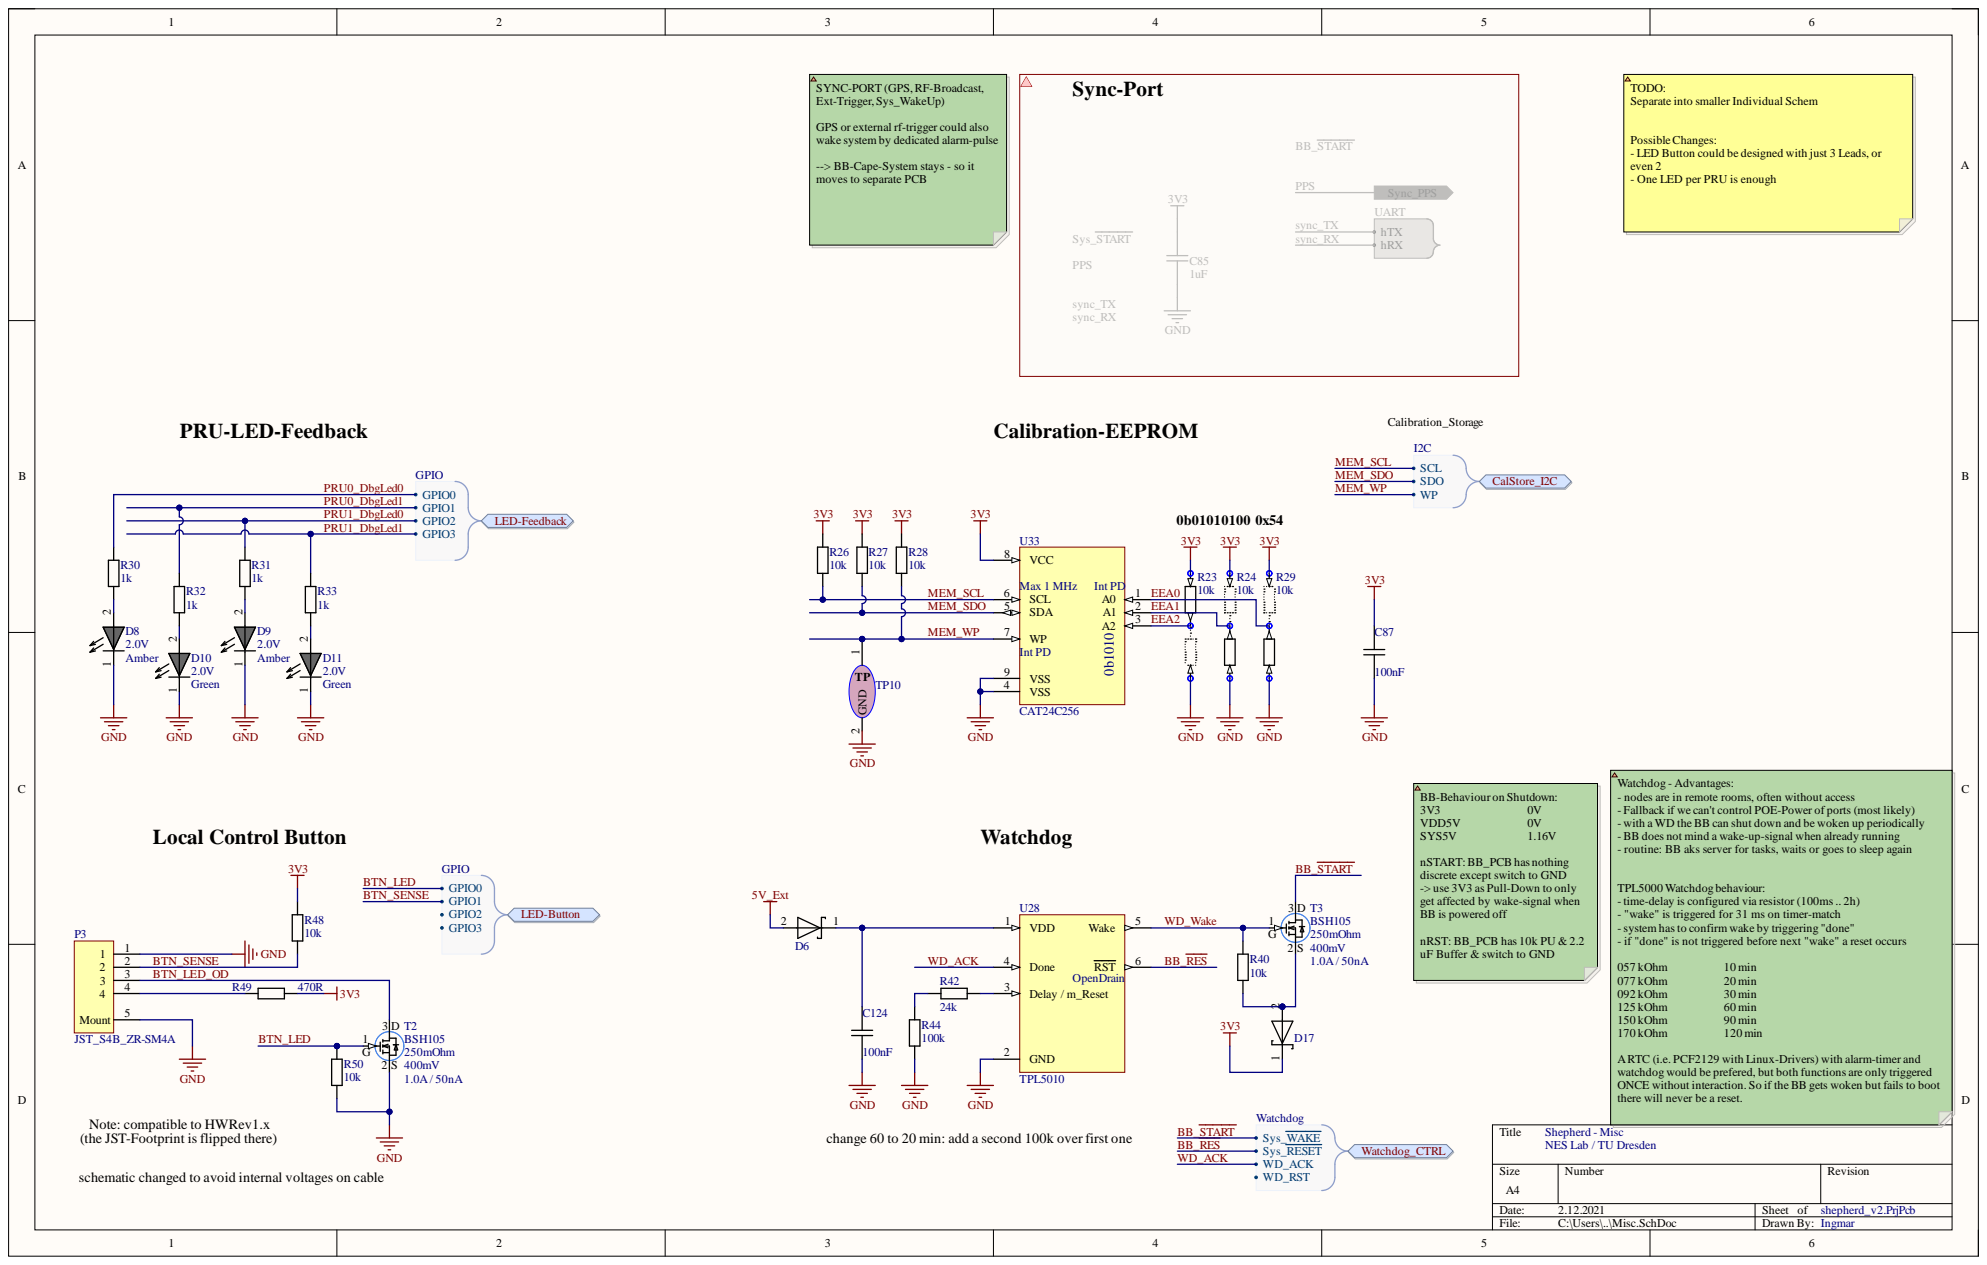
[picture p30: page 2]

SYNC-PORT (GPS,RF-Broadcast,
Ext-Trigger,Sys_WakeUp)

TODO:
Separate into smaller Individual Schem

GPS or external rf-trigger could also
wake system by dedicated alarm-pulse

PossibleChanges:
- LED Button could be designed with just 3 Leads, or
even 2
- One LED per PRU is enough

--> BB-Cape-System stays - so it
moves to separate PCB

Watchdog - Advantages:
- nodes are in remote rooms, often without access
- Fallback if we can't control POE-Power of ports (most likely)
- with a WD the BB can shut down and be woken up periodically
- BB does not mind a wake-up-signal when already running
- routine: BB aks server for tasks, waits or goes to sleep again

BB-Behaviour on Shutdown:

nSTART: BB_PCB has nothing
discrete except switch to GND
-> use 3V3 as Pull-Down to only
get affected by wake-signal when
BB is powered off

TPL5000 Watchdogbehaviour:
- time-delay is configured via resistor (100ms .. 2h)
- "wake" is triggered for 31 ms on timer-match
- system has to confirm wake by triggering "done"
- if "done" is not triggered before next "wake" a reset occurs

nRST: BB_PCB has 10k PU & 2.2
uF Buffer & switch to GND

ARTC (i.e. PCF2129 with Linux-Drivers) with alarm-timer and
watchdog would be prefered, but both functions are only triggered
ONCE without interaction. So if the BB gets woken but fails to boot
there will never be a reset.

Note: compatible to HWRev1.x (the JST-Footprint is flipped there)

change 60 to 20 min: add a second 100k over first one

Shepherd - Misc
NES Lab / TU Dresden

schematic changed to avoid internal voltages on cable

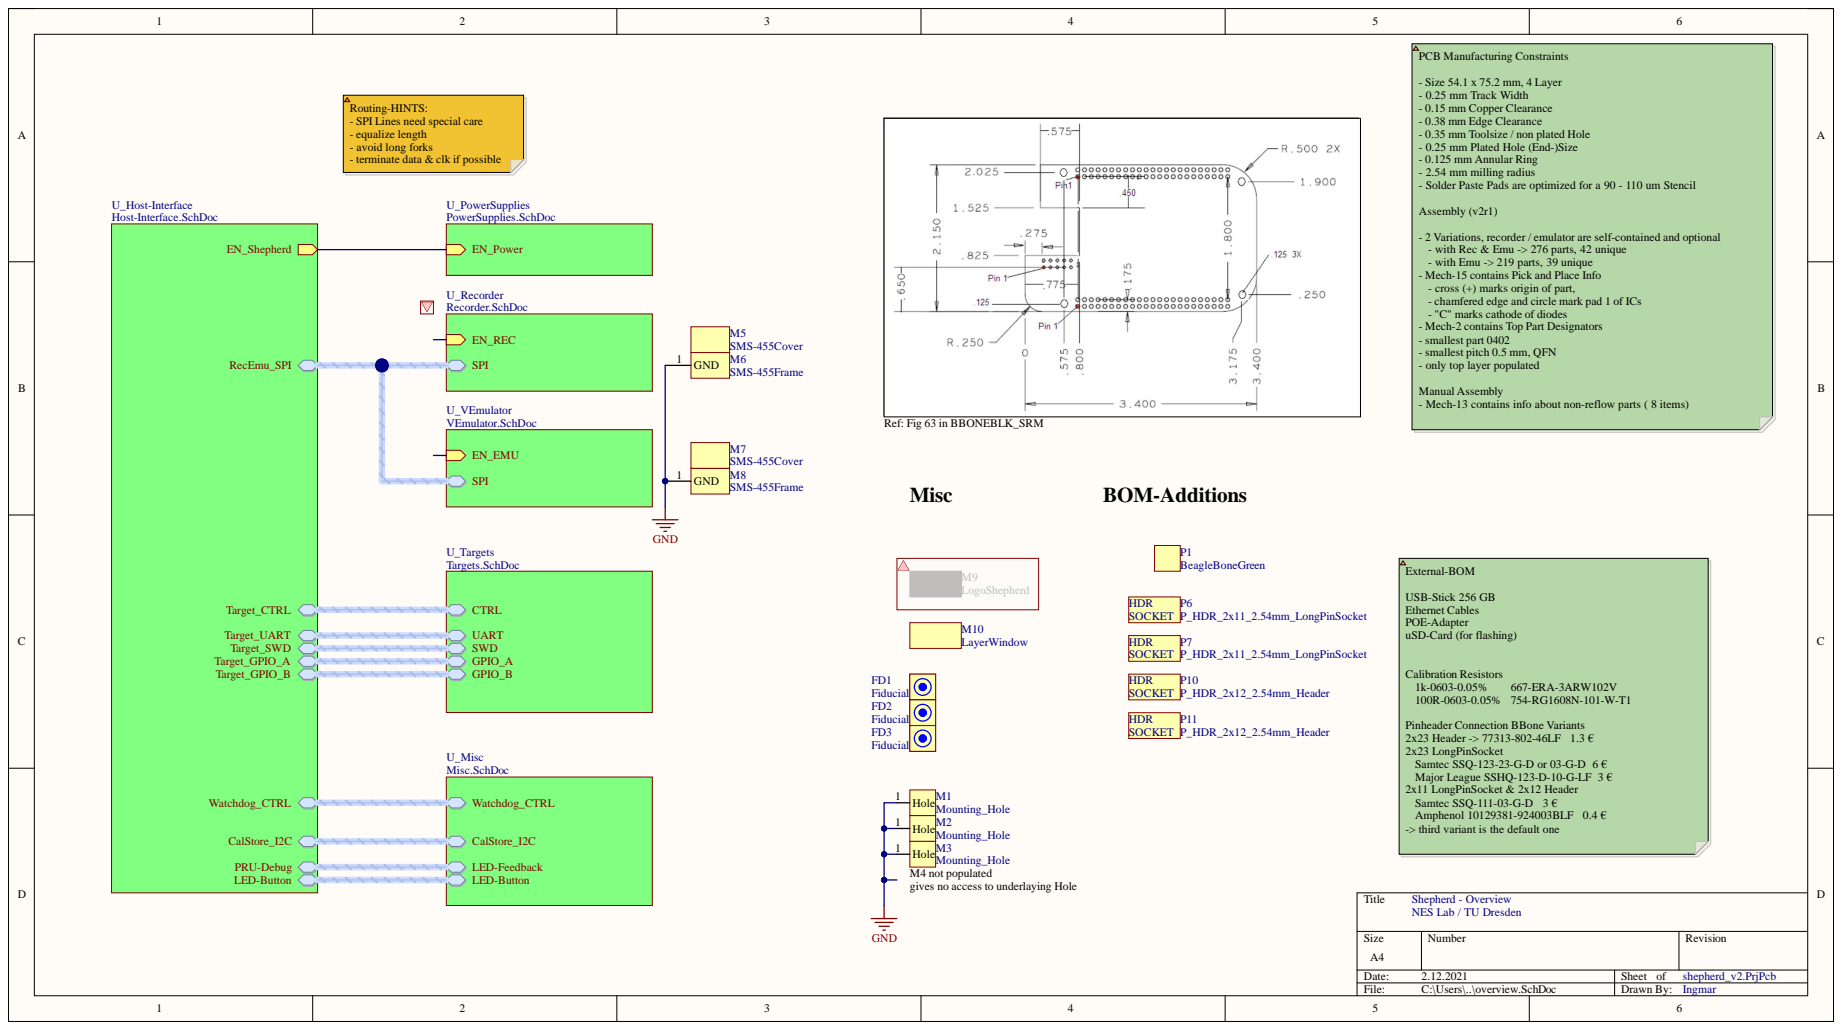
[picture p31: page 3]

and
athode of diode
Top
st pitch 0.5 mm, QF

riant is the de

A4 | r | R evisio n

Date : 2.12.202 1 | She et of shephe rd_v2. P rjP c b
File : C:\Us e r s\. .\ove rvie w . S c hD o c | Dr awn By: Ingma r

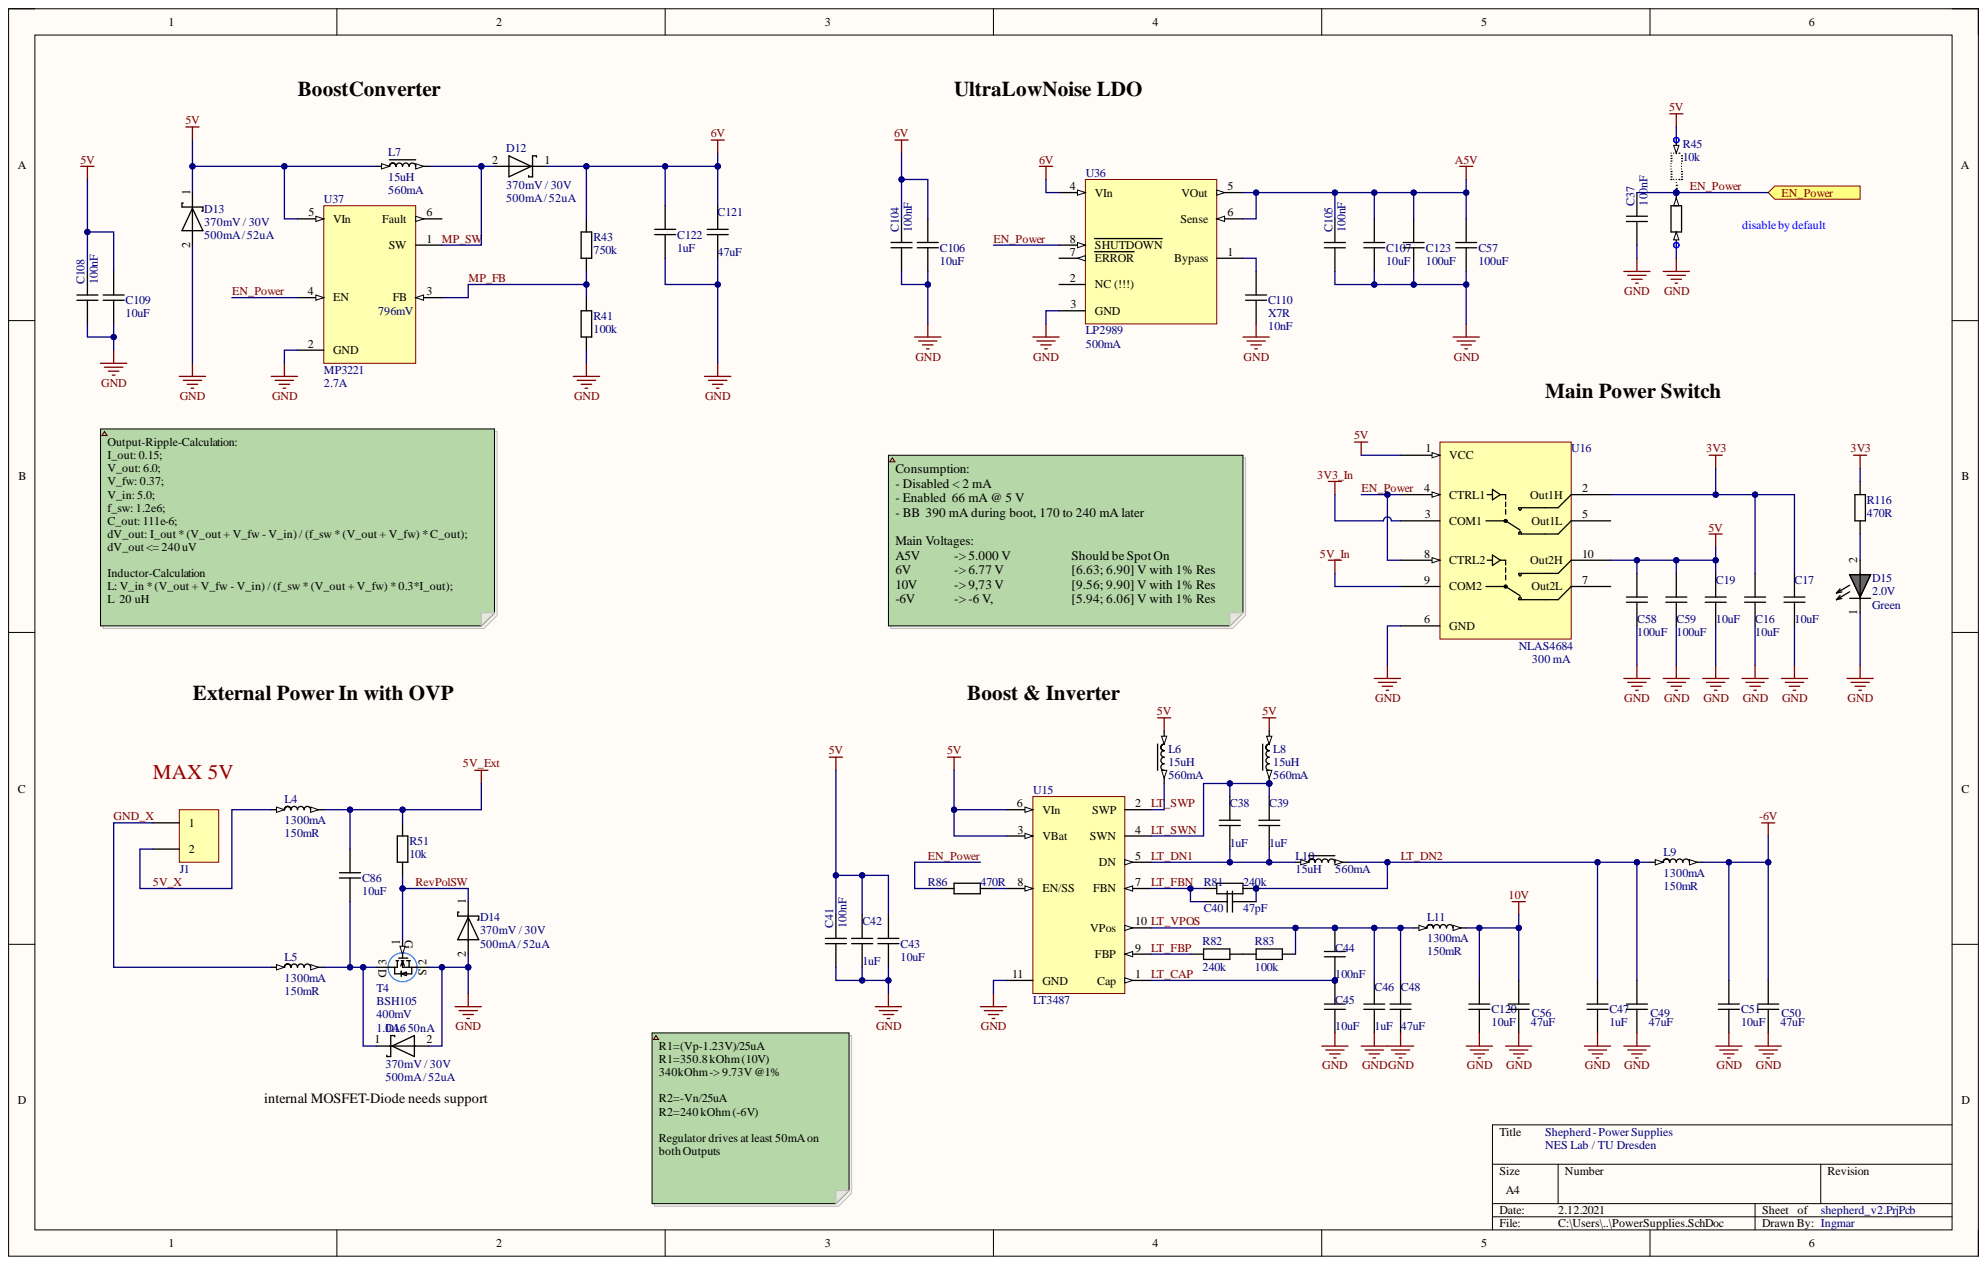
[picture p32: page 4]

Consumption:
- Disabled < 2 mA
- Enabled 66 mA @ 5 V
- BB 390 mA during boot, 170 to 240 mA later

External Power In with OVP

internal MOSFET-Diode needs support

Shepherd - Power Supplies
NES Lab / TU Dresden

Regulator drives at least 50mAon
both Outputs

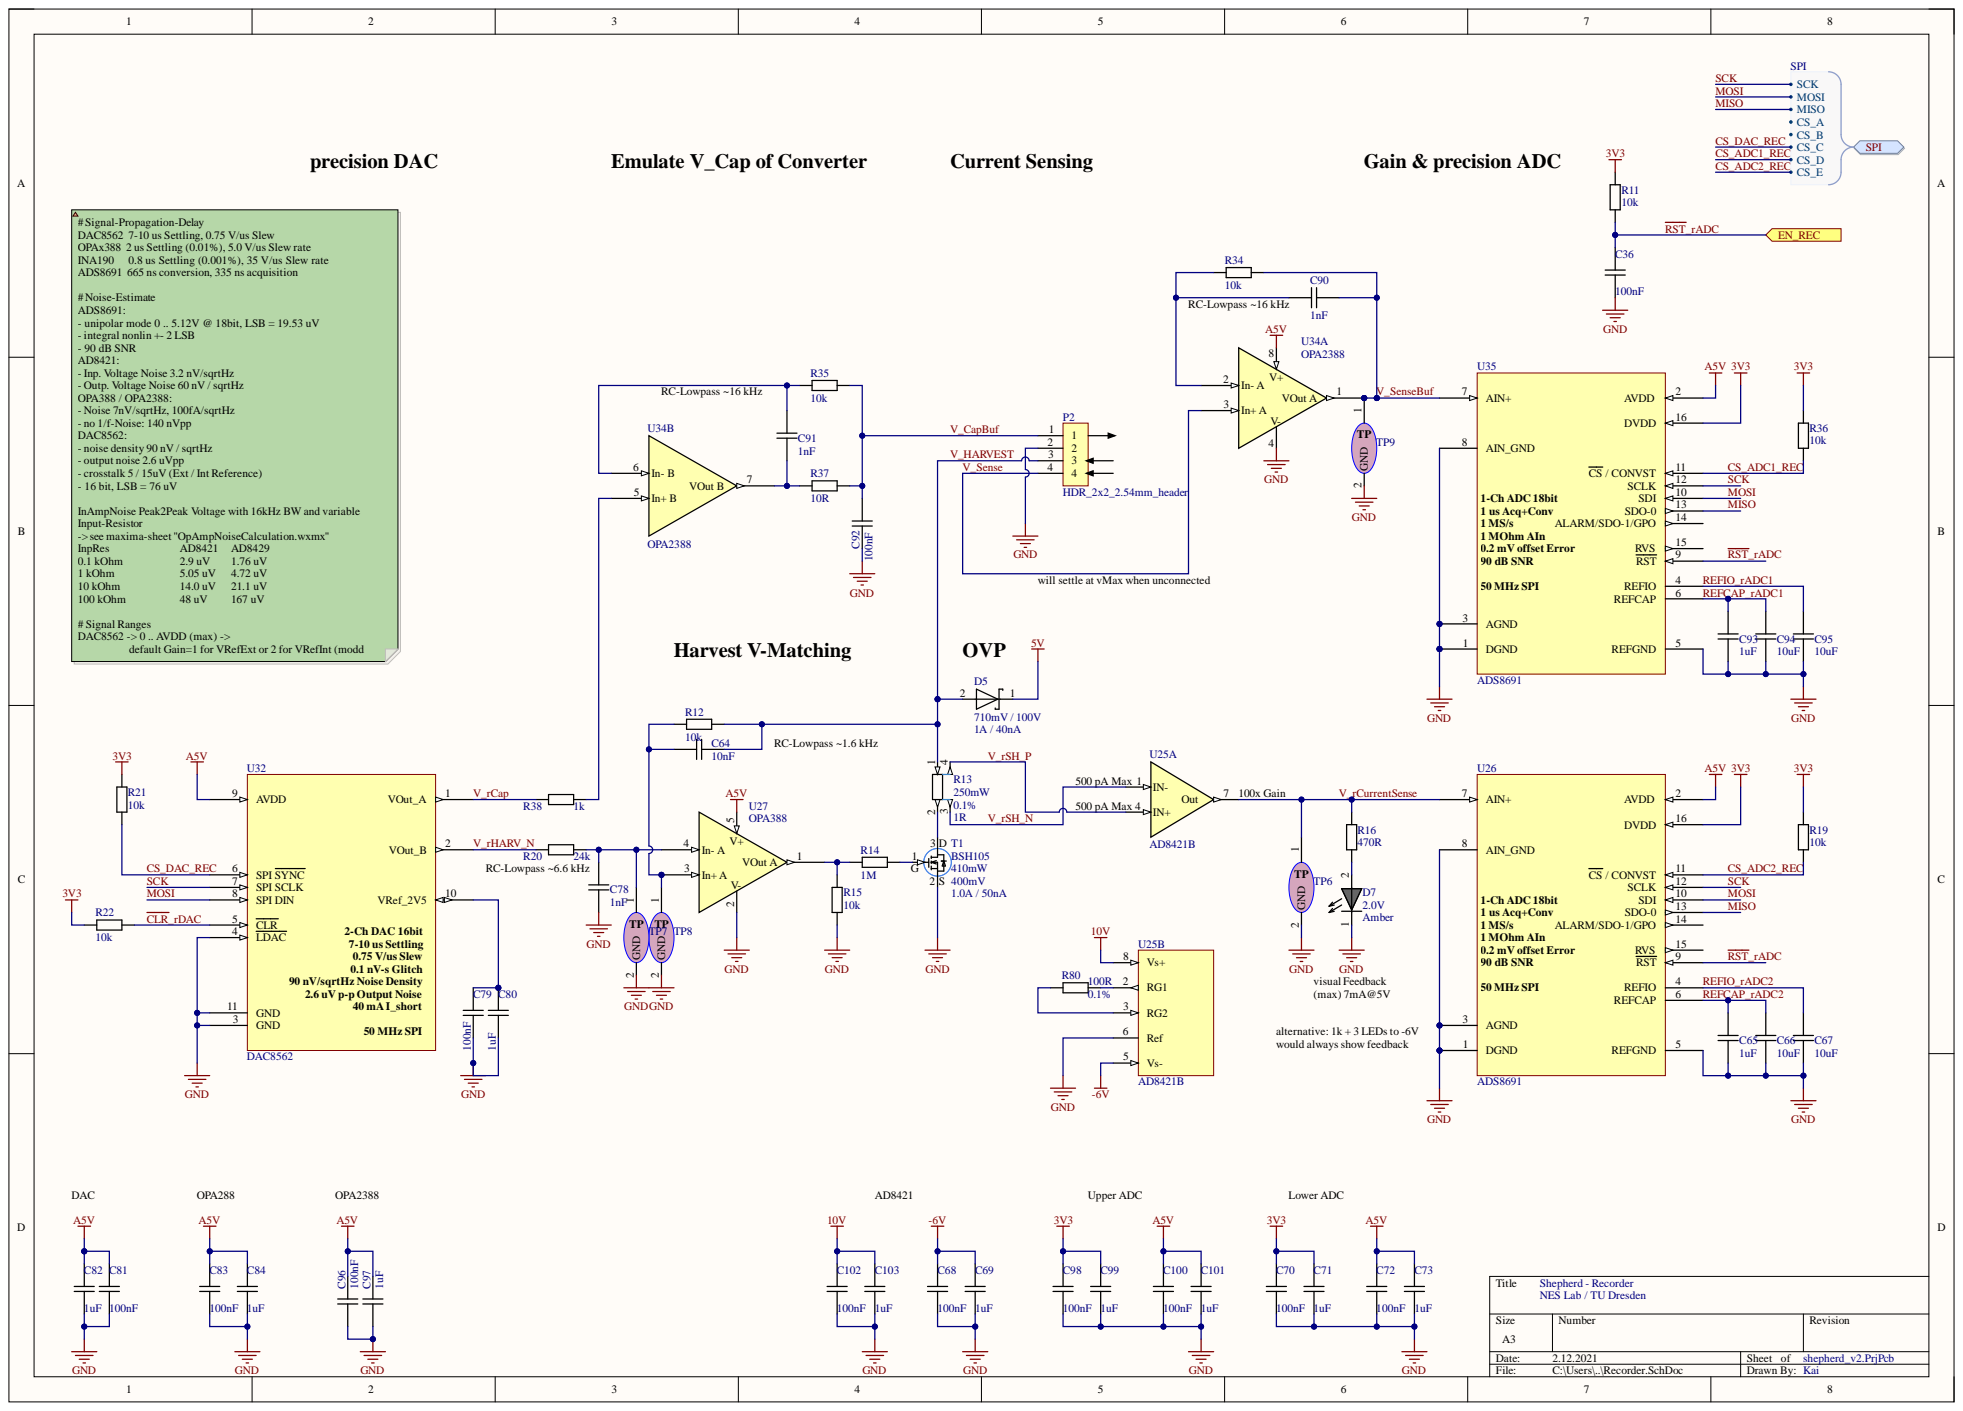
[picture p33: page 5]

# Signal-Propagation-Delay
DAC8562 7-10 us Settling, 0.75 V/us Slew
OPAx388 2 us Settling (0.01%), 5.0 V/us Slew rate
ADS8691 665 ns conversion, 335 ns acquisition

# Noise-Estimate
ADS8691:
- unipolar mode 0 .. 5.12V @ 18bit, LSB = 19.53 uV
- integral nonlin +- 2 LSB
- 90 dB SNR
- Inp. Voltage Noise 3.2 nV/sqrtHz
- Outp. Voltage Noise 60 nV / sqrtHz
OPA388 / OPA2388:
- Noise 7nV/sqrtHz, 100fA/sqrtHz
- no 1/f-Noise: 140 nVpp
DAC8562:
- noise density 90 nV / sqrtHz

- output noise 2.6 uVpp
- crosstalk 5 / 15uV (Ext / Int Reference)
- 16 bit, LSB = 76 uV

InAmpNoise Peak2Peak Voltage with 16kHz BW and variable
Input-Resistor
->see maxima-sheet "OpAmpNoiseCalculation.wxmx"

will settle at vMax when unconnected

default Gain=1 for VRefExt or 2 for VRefInt (modd

90 nV/sqrtHz Noise Density
2.6 uV p-p Output Noise

alternative: 1k + 3 LEDs to -6V
would always show feedback

Shepherd - Recorder
NES Lab / TU Dresden

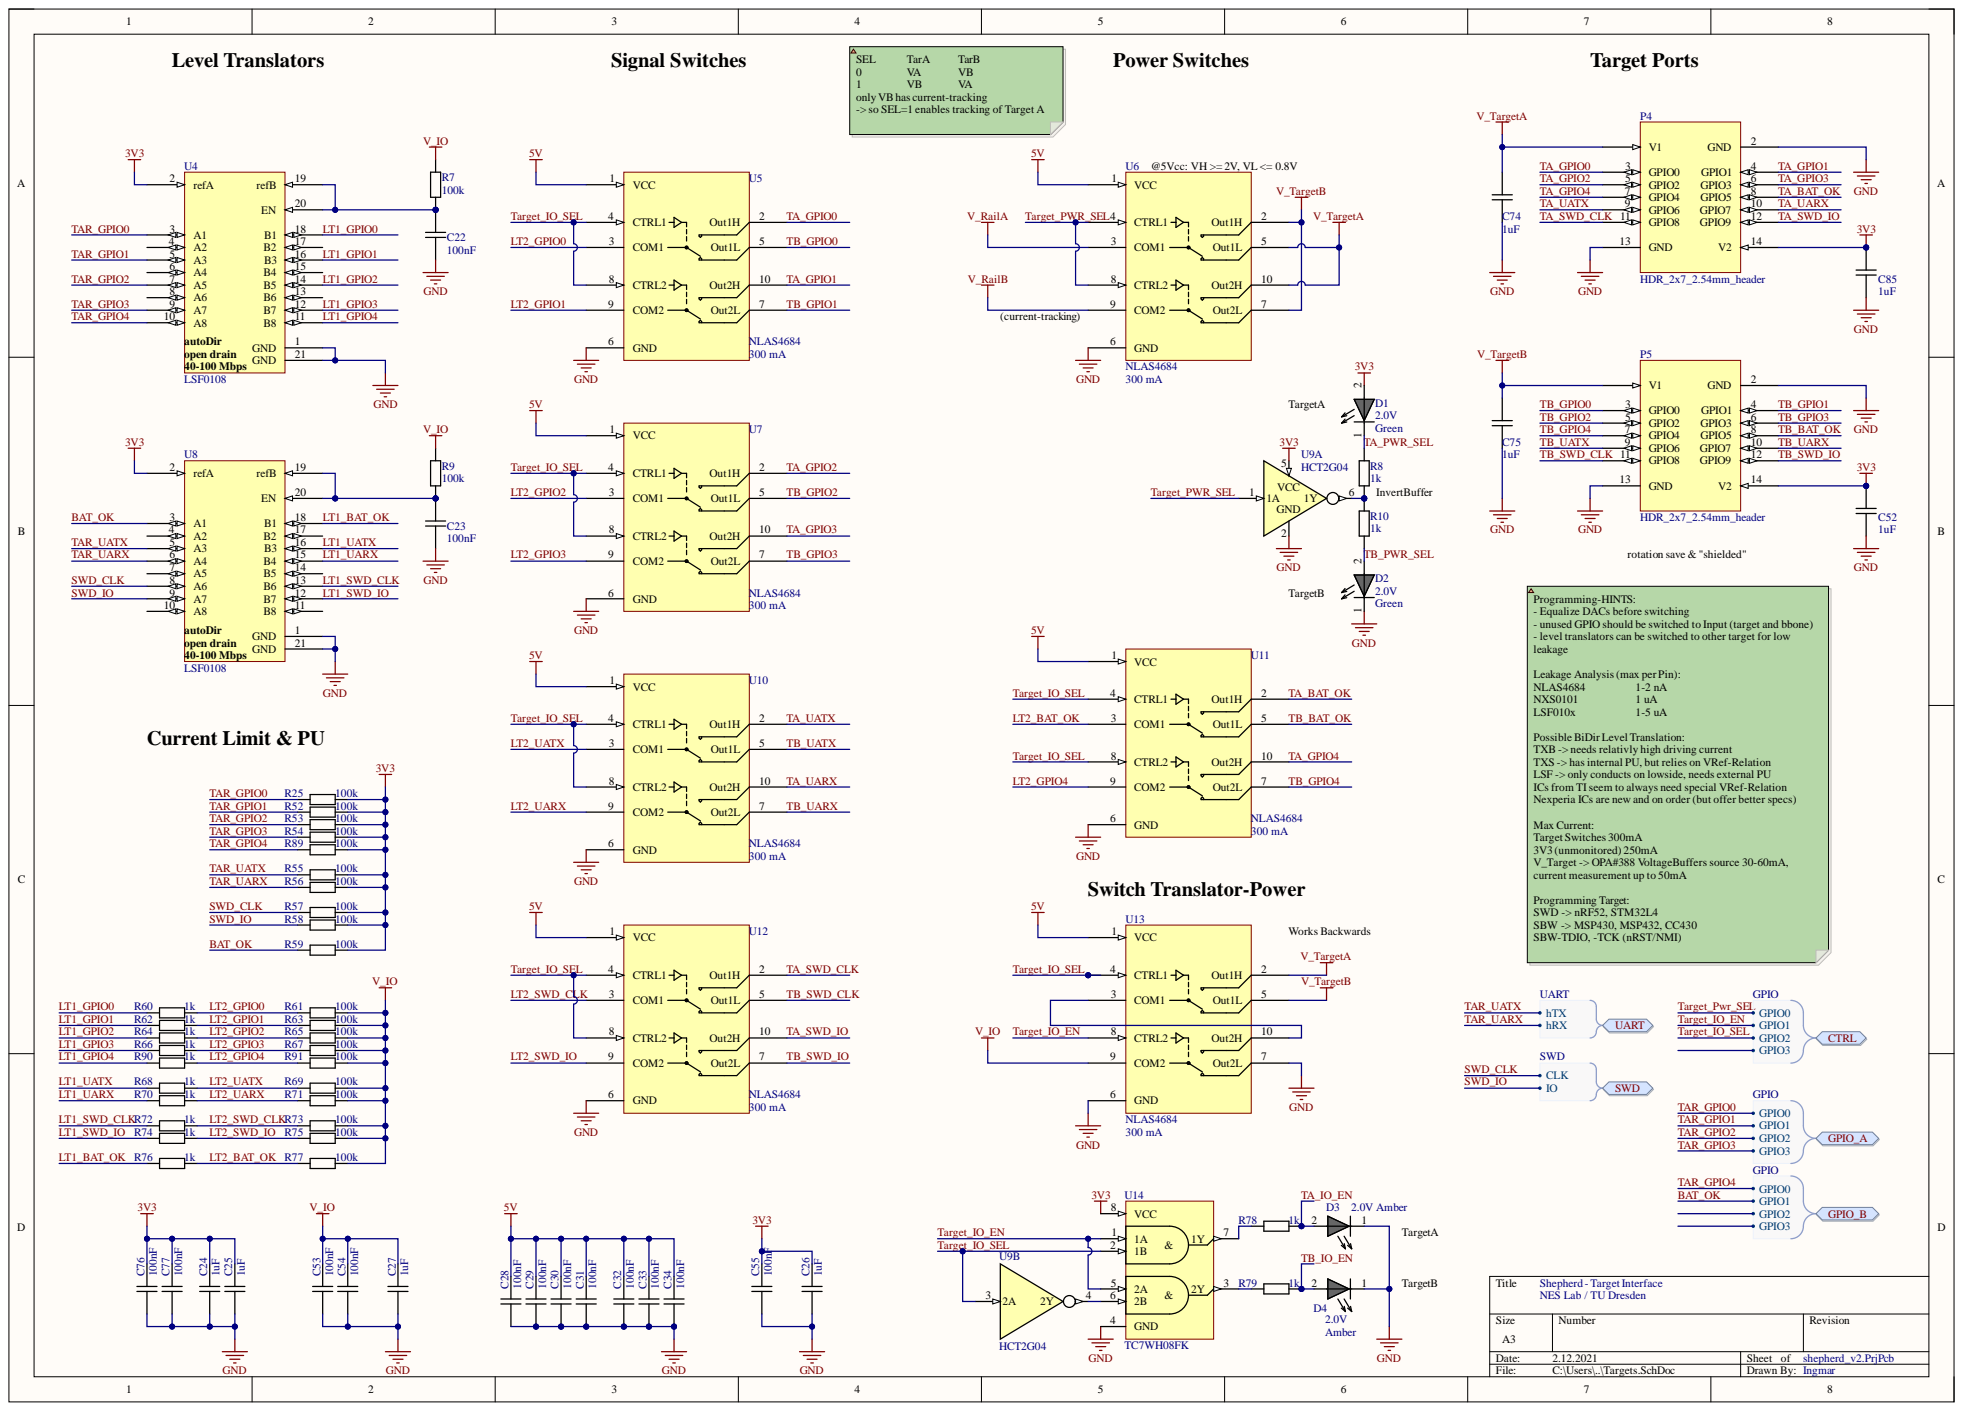
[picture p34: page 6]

s are new and on order

ide, needs external PU

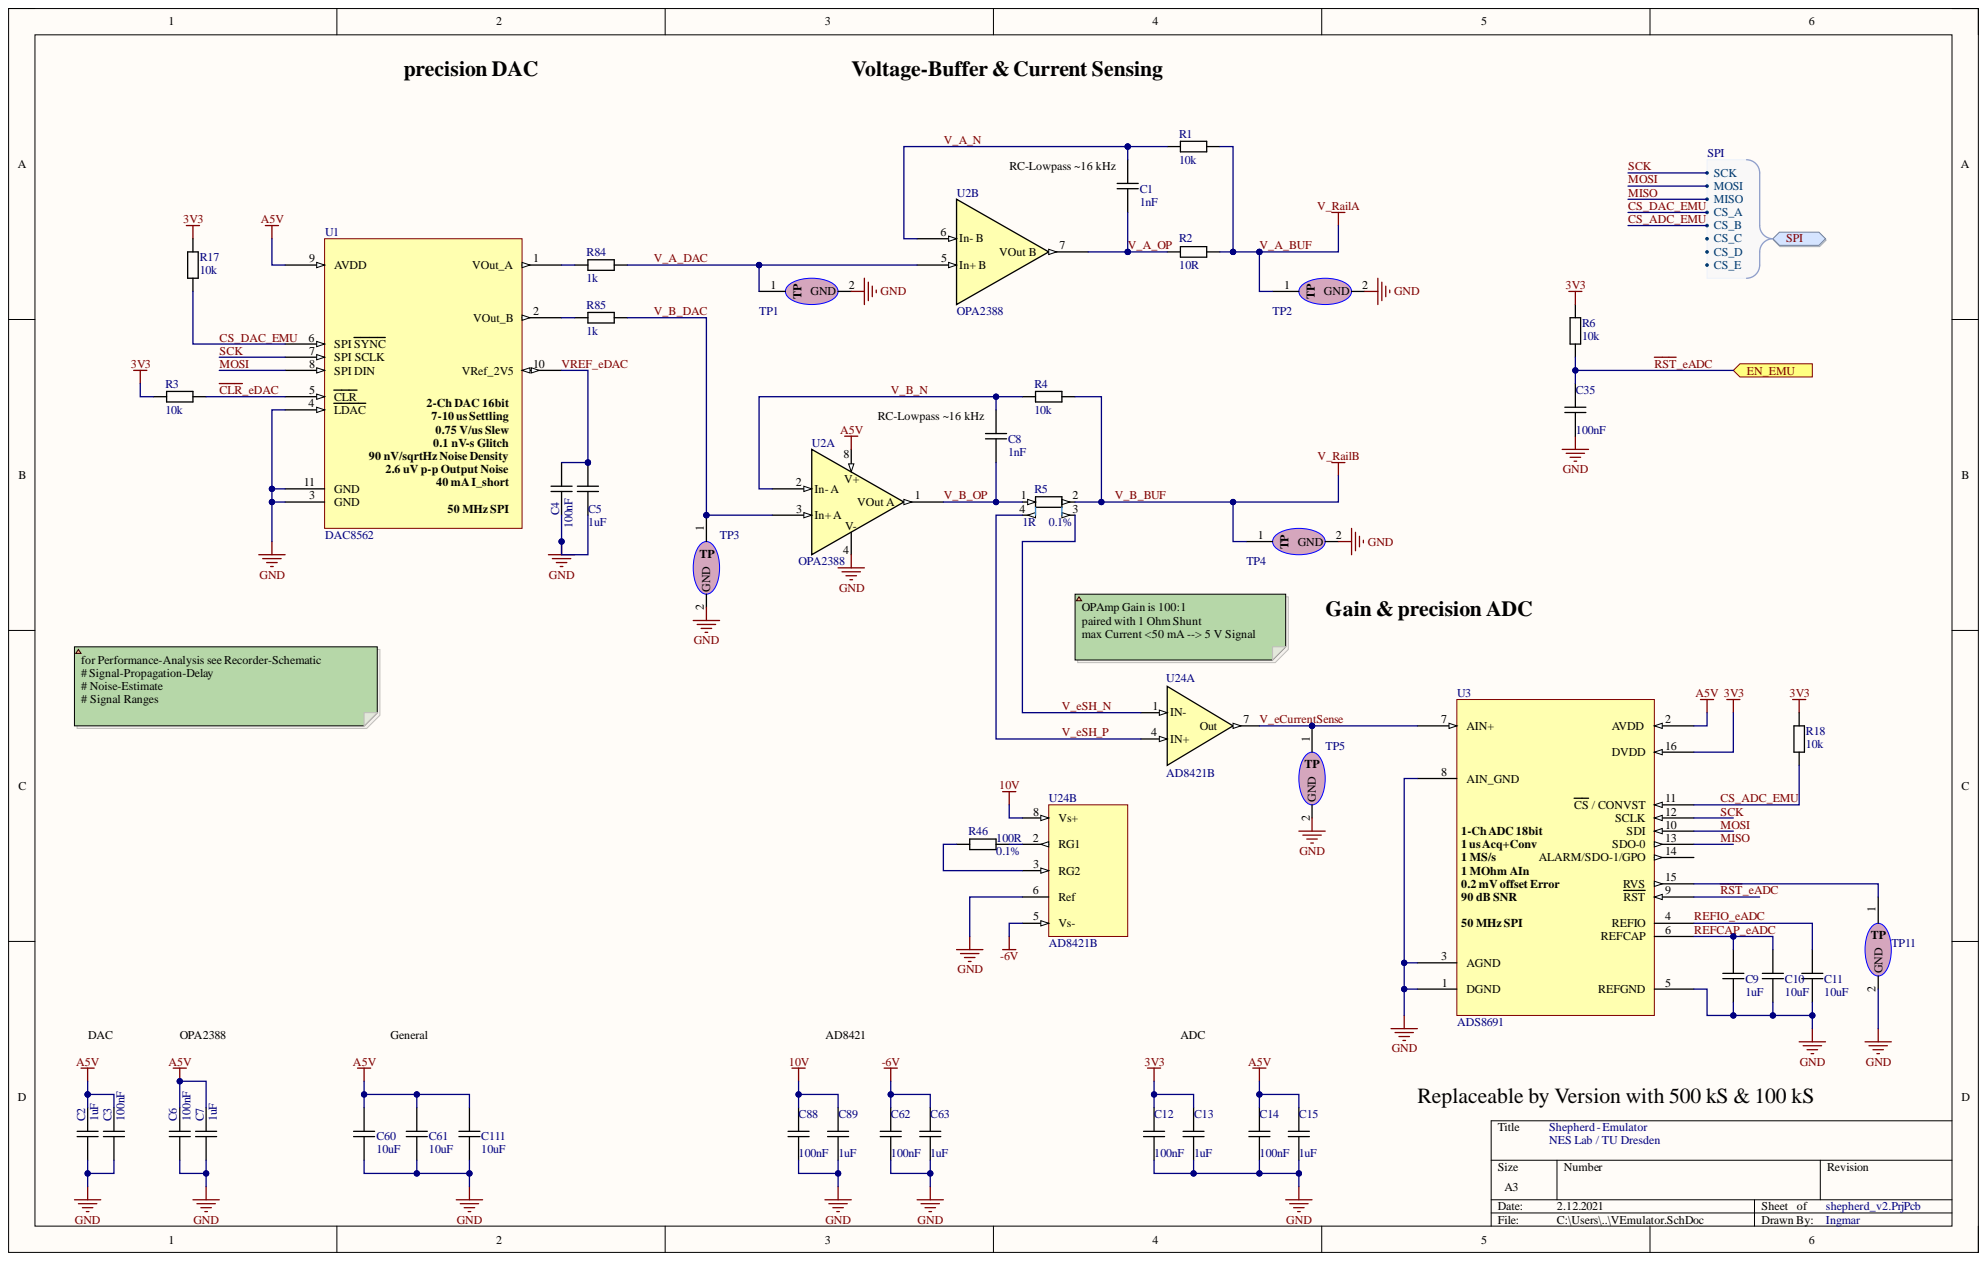
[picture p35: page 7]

90 nV/sqrtHz Noise Density
2.6 uV p-p Output Noise

OPAmp Gain is 100:1
paired with 1 Ohm Shunt
max Current <50 mA --> 5 V Signal

for Performance-Analysis see Recorder-Schematic
# Signal-Propagation-Delay
# Noise-Estimate
# Signal Ranges

Replaceable by Version with 500 kS & 100 kS

Shepherd - Emulator
NES Lab / TU Dresden

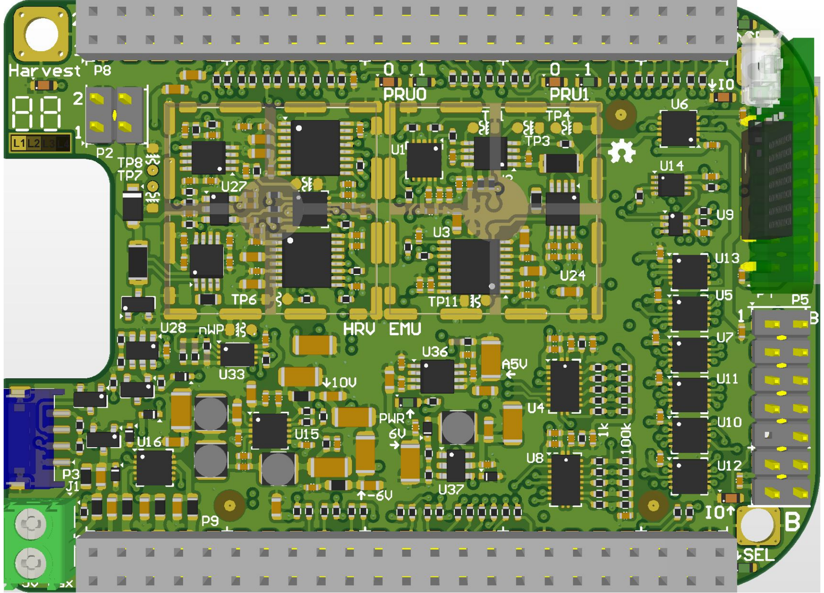
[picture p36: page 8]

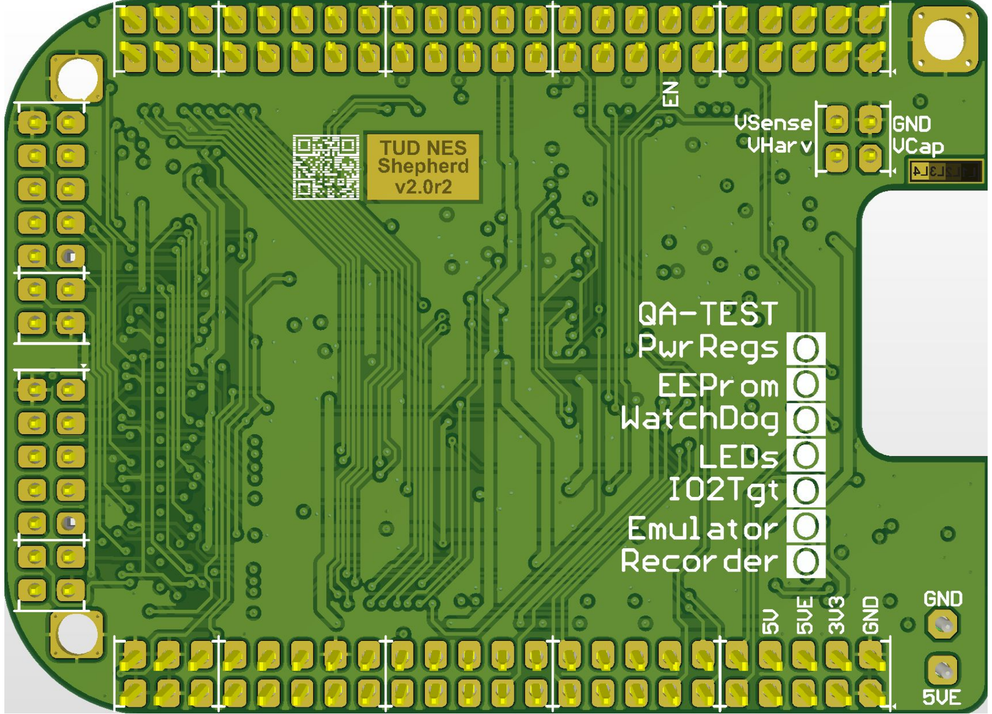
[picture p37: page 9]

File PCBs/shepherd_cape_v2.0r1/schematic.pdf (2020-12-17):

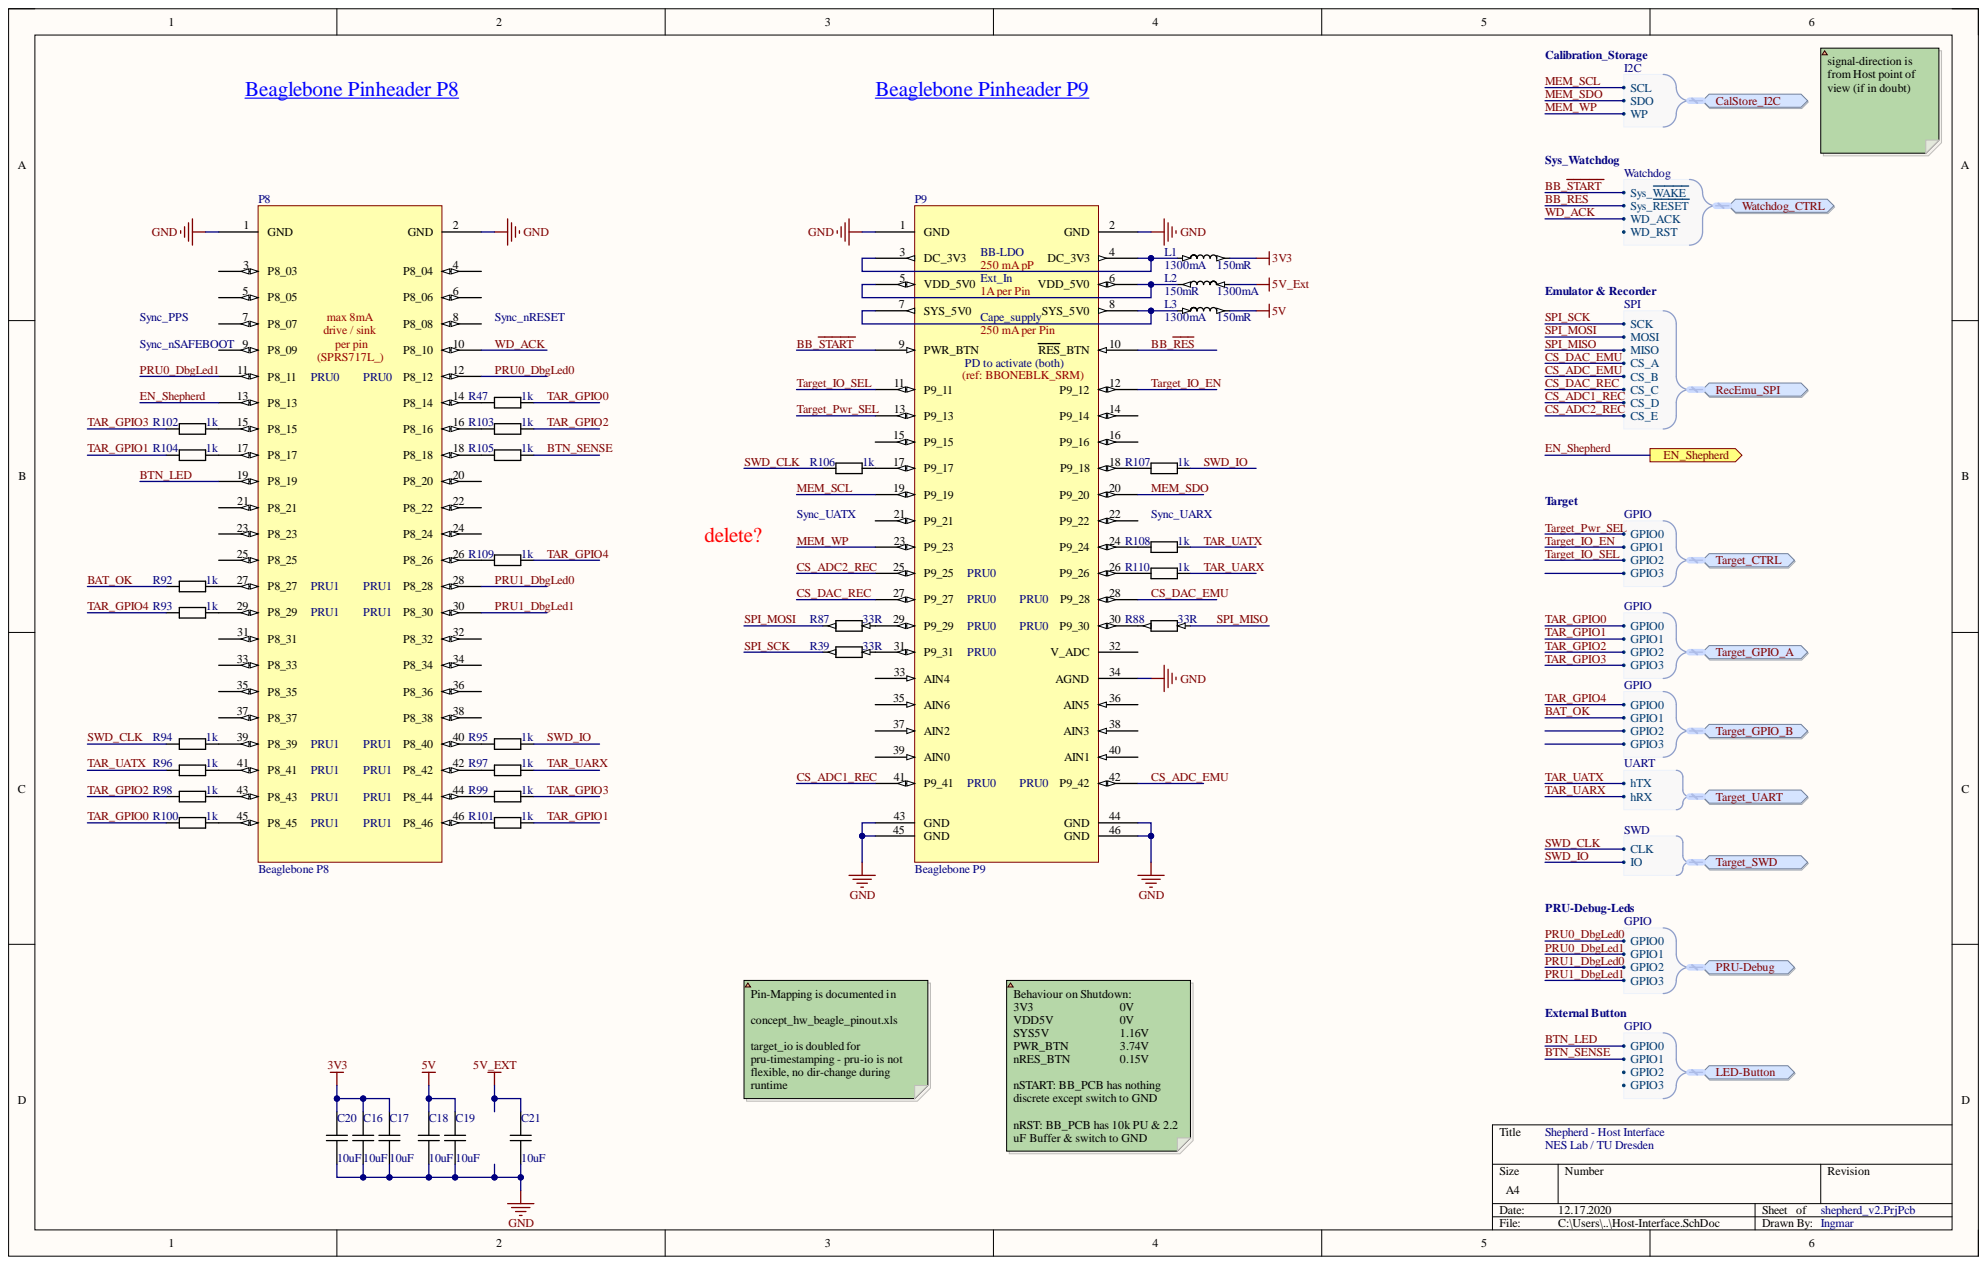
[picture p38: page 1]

signal-direction is
from Host point of
view (if in doubt)

PD to activate (both)
(ref: BBONEBLK_SRM)

Pin-Mapping is documented in

target_io is doubled for
pru-timestamping - pru-io is not
flexible, no dir-change during
runtime

nSTART: BB_PCB has nothing
discrete except switch to GND

nRST: BB_PCB has 10k PU & 2.2
uF Buffer & switch to GND

Shepherd - Host Interface
NES Lab / TU Dresden

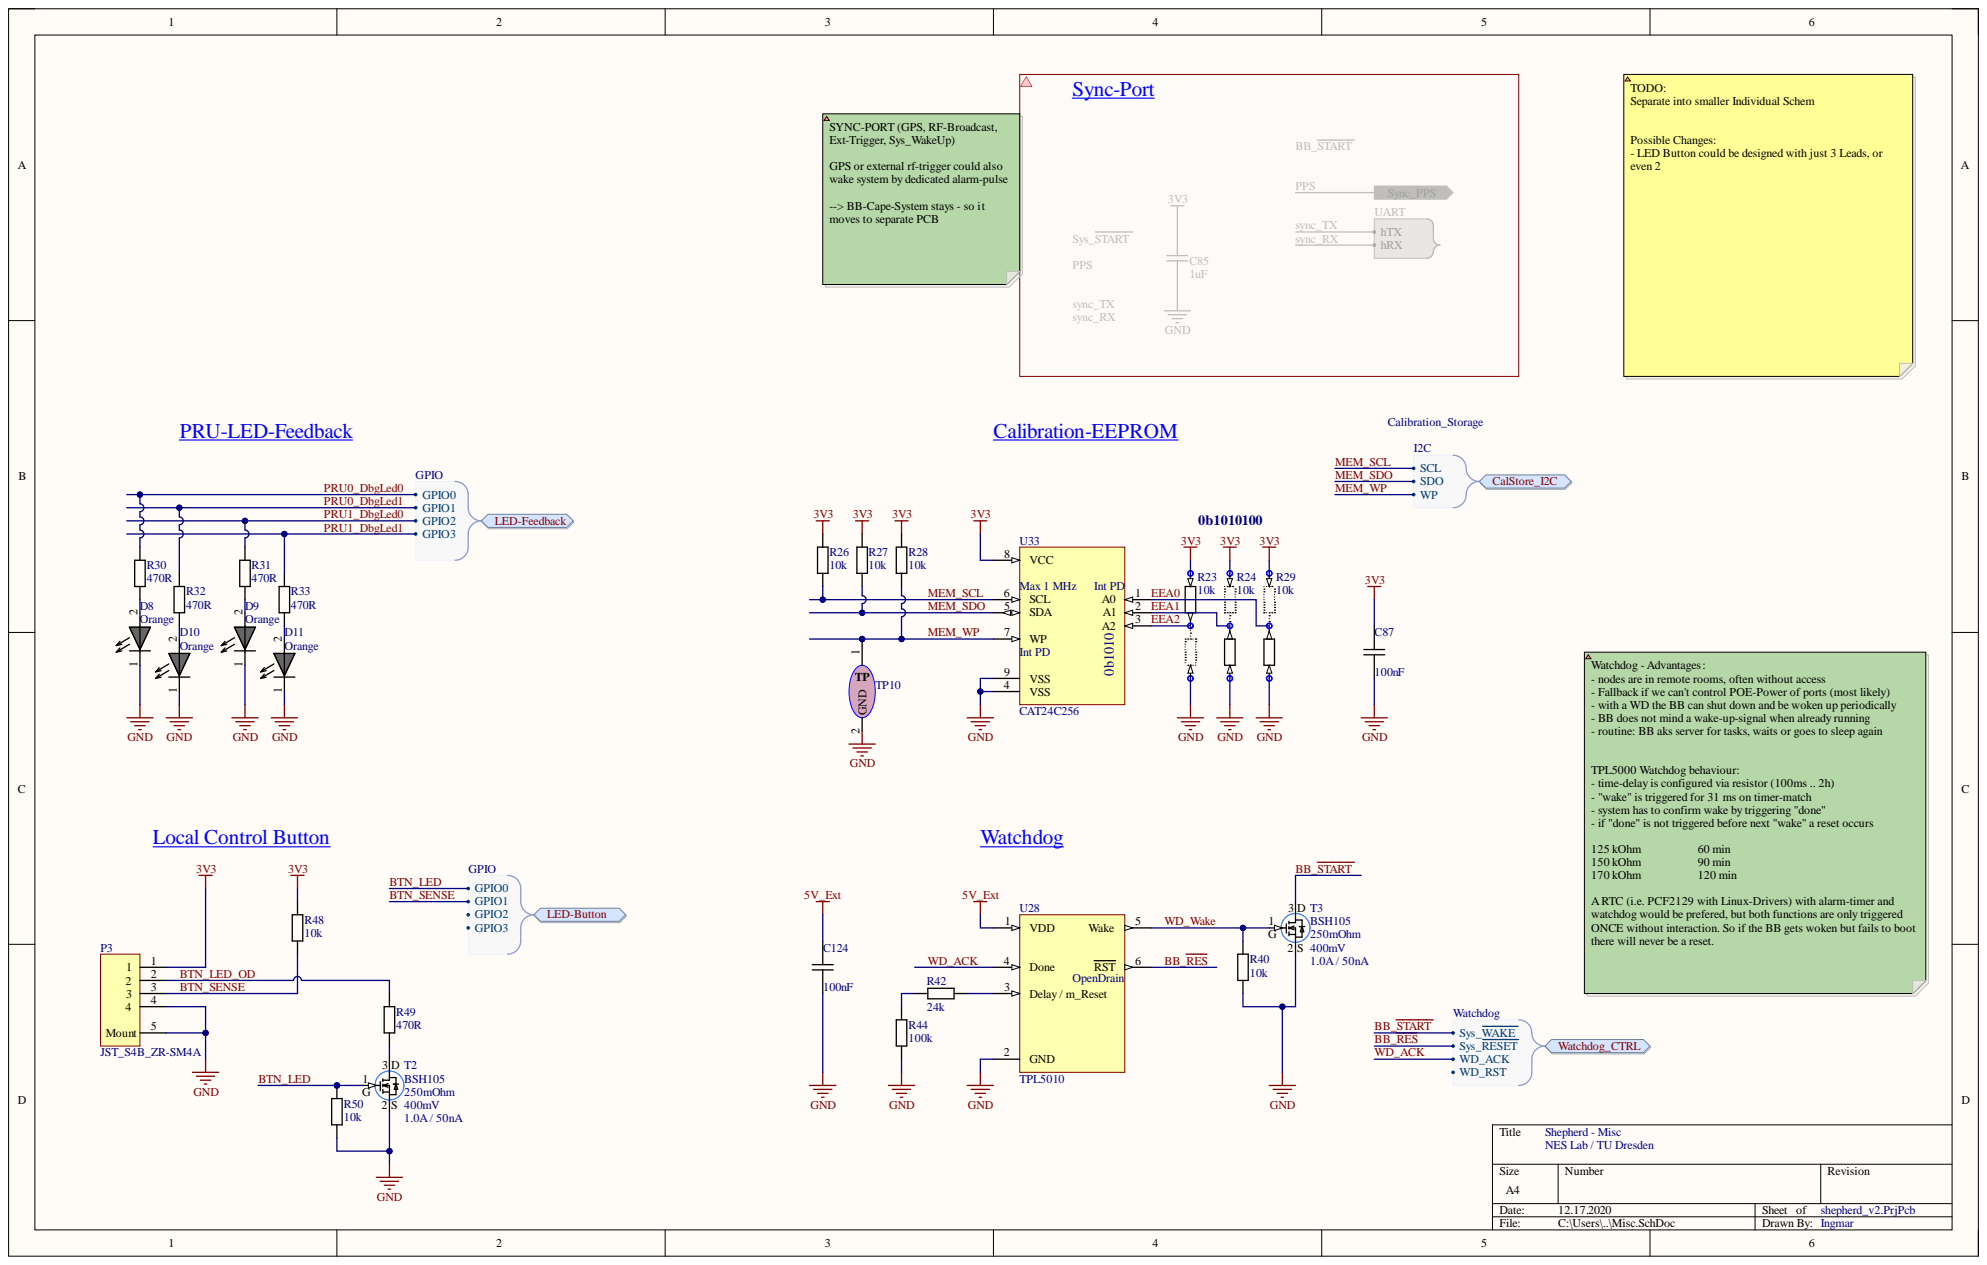
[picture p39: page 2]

TODO:
Separate into smaller Individual Schem

SYNC-PORT (GPS, RF-Broadcast,
Ext-Trigger, Sys_WakeUp)

Possible Changes:
- LED Button could be designed with just 3 Leads, or
even 2

GPS or external rf-trigger could also
wake system by dedicated alarm-pulse

--> BB-Cape-System stays - so it
moves to separate PCB

Watchdog - Advantages:
- nodes are in remote rooms, often without access
- Fallback if we can't control POE-Power of ports (most likely)
- with a WD the BB can shut down and be woken up periodically
- BB does not mind a wake-up-signal when already running
- routine: BB aks server for tasks, waits or goes to sleep again

TPL5000 Watchdog behaviour:
- time-delay is configured via resistor (100ms .. 2h)
- "wake" is triggered for 31 ms on timer-match
- system has to confirm wake by triggering "done"
- if "done" is not triggered before next "wake" a reset occurs

ARTC (i.e. PCF2129 with Linux-Drivers) with alarm-timer and
watchdog would be prefered, but both functions are only triggered
ONCE without interaction. So if the BB gets woken but fails to boot
there will never be a reset.

Shepherd - Misc
NES Lab / TU Dresden

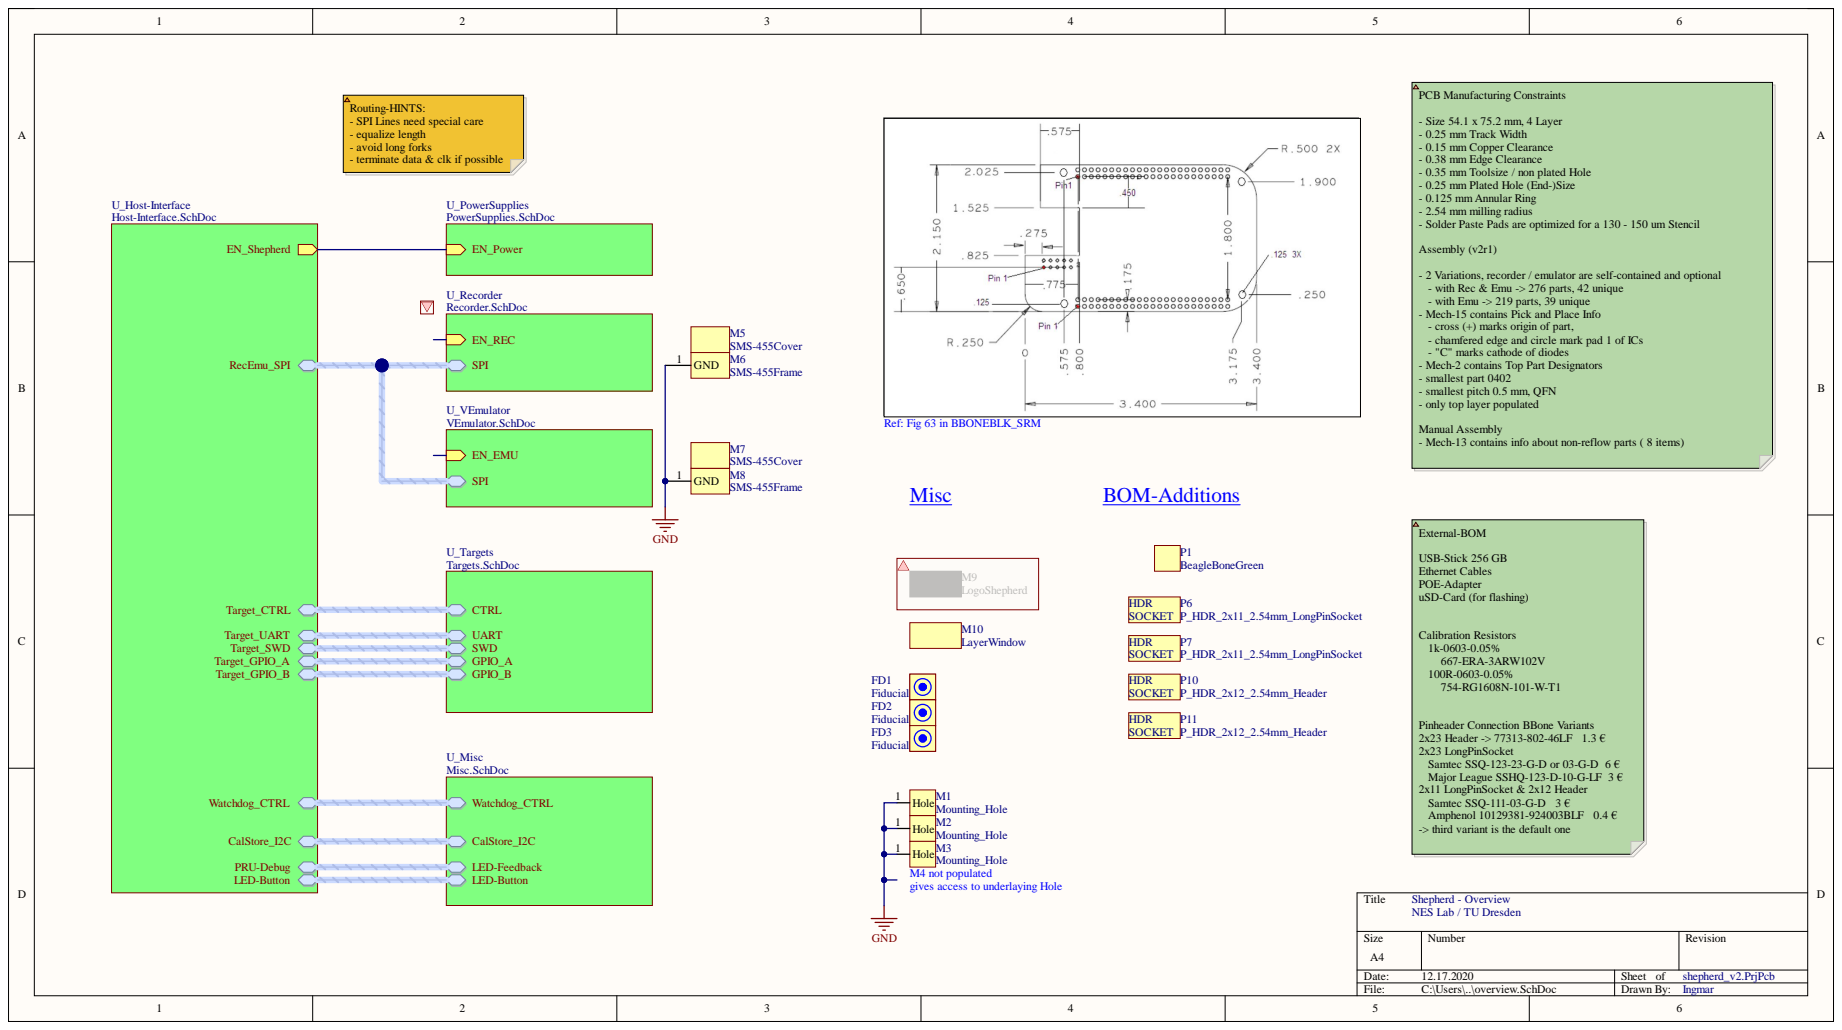
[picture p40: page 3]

rks origin of pa

A4 | r | R evision

Date : 12.17.202 0 | S he et of s heph e rd_v2. P rjP c b
File : C:\U s e r s\. .\ove rvie w . S c hDoc | Dr a w n By: Ing ma r


External Power In with OVP

Shepherd - Power Supplies
NES Lab / TU Dresden

Regulator drives at least 50mAon
both Outputs


# Signal-Propagation-Delay
DAC8562 7-10 us Settling, 0.75 V/us Slew
OPAx388 2 us Settling (0.01%), 5.0 V/us Slew rate
ADS8691 665 ns conversion, 335 ns acquisition

# Noise-Estimate
ADS8691:
- unipolar mode 0 .. 5.12V @ 18bit, LSB = 19.53 uV
- integral nonlin +- 2 LSB
- 90 dB SNR
- Inp. Voltage Noise 3.2 nV/sqrtHz
- Outp. Voltage Noise 60 nV / sqrtHz
OPA388 / OPA2388:
- Noise 7nV/sqrtHz, 100fA/sqrtHz
- no 1/f-Noise: 140 nVpp
DAC8562:

- noise density 90 nV / sqrtHz
- output noise 2.6 uVpp
- crosstalk 5 / 15uV (Ext / Int Reference)
- 16 bit, LSB = 76 uV

InAmpNoise Peak2Peak Voltage with 16kHz BW and variable
Input-Resistor
-> see maxima-sheet "OpAmpNoiseCalculation.wxmx"

default Gain=1 for VRefExt or 2 for VRefInt (modd

90 nV/sqrtHz Noise Density
2.6 uV p-p Output Noise

Shepherd - Recorder
NES Lab / TU Dresden


s are new and on order (bu


90 nV/sqrtHz Noise Density
2.6 uV p-p Output Noise

OPAmp Gain is 100:1
paired with 1 Ohm Shunt
max Current <50 mA--> 5 V Signal

for Performance-Analysis see Recorder-Schematic
# Signal-Propagation-Delay
# Noise-Estimate
# Signal Ranges

REFCAP_eADC

Replaceable by Version with 500 kS & 100 kS

Shepherd - Emulator
NES Lab / TU Dresden





















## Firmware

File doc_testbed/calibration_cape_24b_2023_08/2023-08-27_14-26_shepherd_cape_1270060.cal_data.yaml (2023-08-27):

datatype: CalibrationCape
created: 2023-08-27 14:26:43.477883
parameters:
  cape:
    serial_number: '1270060'
  host: sheep0
  harvester:
    dac_V_Hrv:
      gain: 7.623909708491015e-05
      offset: 0.0009349204131494648
    dac_V_Sim:
      gain: 7.623021875590802e-05
      offset: 0.0009474486797842463
    adc_V_Sense:
      gain: 1.9514250274983104e-05
      offset: 0.000197869159144215
    adc_C_Hrv:
      gain: 2.0280991775527926e-07
      offset: 4.59726964940595e-06
  emulator:
    dac_V_A:
      gain: 7.623352215053642e-05
      offset: 0.0005500019339295115
    dac_V_B:
      gain: 7.623319998927178e-05
      offset: 0.0001261384857482728
    adc_C_A:
      gain: 2.026111492056382e-07
      offset: -0.0001230995197914436
    adc_C_B:
      gain: 2.0267495645714652e-07
      offset: -0.00012300254794526174

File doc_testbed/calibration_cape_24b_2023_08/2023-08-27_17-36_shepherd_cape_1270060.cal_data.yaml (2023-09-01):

datatype: CalibrationCape
created: 2023-08-27 17:36:47.891694
parameters:
  cape:
    serial_number: '1270060'
  host: sheep0
  harvester:
    dac_V_Hrv:
      gain: 7.623790497180501e-05
      offset: 0.0009348925134797792
    dac_V_Sim:
      gain: 7.622915601529995e-05
      offset: 0.0009560635045839927
    adc_V_Sense:
      gain: 1.951360957126691e-05
      offset: 0.00018741670371724695
    adc_C_Hrv:
      gain: 2.0281329944858892e-07
      offset: 4.800576011840772e-06
  emulator:
    dac_V_A:
      gain: 7.623233447758286e-05
      offset: 0.0005624870034022234
    dac_V_B:
      gain: 7.623203614798924e-05
      offset: 0.000130564029780178
    adc_C_A:
      gain: 2.0261488549933603e-07
      offset: -0.00012302249788977843
    adc_C_B:
      gain: 2.0267129692415158e-07
      offset: -0.00012290219206302676

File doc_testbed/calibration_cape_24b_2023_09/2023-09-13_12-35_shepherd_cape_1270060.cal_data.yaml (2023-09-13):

datatype: CalibrationCape
created: 2023-09-13 12:35:43.250035
parameters:
  cape:
    serial_number: '1270060'
  host: sheep0
  emulator: # 2R, 210, GND-ref
    dac_V_A:
      gain: 7.623795873856053e-05
      offset: 0.0005326753558823061
    dac_V_B:
      gain: 7.623478404268054e-05
      offset: 0.00010758830038160028
    adc_C_A:
      gain: 2.025642355569067e-07
      offset: -1.3145193654979202e-05
    adc_C_B:
      gain: 2.0264663731212524e-07
      offset: -1.3337394342311827e-05
  harvester:  # OLD
    dac_V_Hrv:
      gain: 7.623790497180501e-05
      offset: 0.0009348925134797792
    dac_V_Sim:
      gain: 7.622915601529995e-05
      offset: 0.0009560635045839927
    adc_V_Sense:
      gain: 1.951360957126691e-05
      offset: 0.00018741670371724695
    adc_C_Hrv:
      gain: 2.0281329944858892e-07
      offset: 4.800576011840772e-06

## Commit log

2020-07-09 concepts contain at least current requirements
2020-07-10 big part of schematic analysis
    [12_concept_hw_beagle_pinout.xlsx]
2020-07-25 fixed device tree and earned a warning
2020-10-08 update concept with latest rf measurement and other progress
    [10_cfaed_ethernet_ports.ods, 10_rf_measurements.ods]
2020-10-12 update requierments
    [10_cfaed_ethernet_ports.ods]
2020-10-15 current BBAI tests
2020-11-20 Update 21_hw_design_cape.rst
    latest pcb changes
2020-12-17 add hardware files
    [Bill of Materials-shepherd_target_nRF.xlsx, Bill of Materials-shepherd_v2.xlsx, Bill of Materials-shepherd_v2_emu_only.xlsx, Bill of Materials-shepherd_v2_emu_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]
2021-01-27 Update 21_hw_design_cape.rst
    latest pcb progress
2021-01-27 Create List of BB MAC-Addresses.ods
    [List of BB MAC-Addresses.ods]
2021-02-12 new cape v2r2
    [Bill of Materials-shepherd_v2r2_emu_only.xlsx, Bill of Materials-shepherd_v2r2_emu_only_for_PNP.xlsx, Bill of Materials-shepherd_v2r2_emu_rec.xlsx, shepherd_pc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]
2021-02-14 small improvement on pcb
    [shepherd_pcb_v2r2_Copper_Signal_1.gbr, shepherd_pcb_v2r2_Copper_Signal_2.gbr, shepherd_pcb_v2r2_Copper_Signal_Bot.gbr, shepherd_pcb_v2r2_Copper_Signal_Top.gbr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]
2021-02-14 add production files
    [Bill of Materials-shepherd_v2r2_emu_only_for_PNP.ods, Pick Place for shepherd_pcb_v2r2_InCircuit.csv, Pick Place for shepherd_pcb_v2r2_InCircuit.ods]
2021-02-14 update assembly data
2021-02-27 fix problem - in theory
    [leveltranslator isolated.SchDoc]
2021-02-28 finish gpio-bug
    [leveltranslator isolated.SchDoc]
2021-03-02 verify theory
    [leveltranslator isolated.SchDoc]
2021-03-23 add finished shepherd cape
    [Bill of Materials-shepherd_v2.1r0_emu_only.xlsx, Bill of Materials-shepherd_v2.1r0_emu_rec.xlsx, shepherd_pcb_v2.1r0_Copper_Signal_1.gbr, shepherd_pcb_v2.1r0_C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]
2021-03-23 cleaner folder structure
    [Bill of Materials-shepherd_target_nRF.xlsx, Bill of Materials-shepherd_v2.xlsx, Bill of Materials-shepherd_v2_emu_only.xlsx, Bill of Materials-shepherd_v2_emu_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]
2021-04-11 pSpice Simulation of Recorder
    [shepherd_recorder_opDrain.dsn]
2021-04-11 Update Bill of Materials-shepherd_target_nRF.xlsx
    [Bill of Materials-shepherd_target_nRF.xlsx]
2021-04-28 add pcb pics
2021-06-27 newest design files
    [Emulator.SchDoc, Host-Interface.SchDoc, LevelTranslators.SchDoc, Misc.SchDoc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]
2021-06-27 newest production files
    [Bill of Materials-shepherd_v2.2_emu_rec.xlsx, Bill of Materials-shepherd_v2.2_emu_smd.xlsx, shepherd_pcb_v2.2_Copper_Signal_1.gbr, shepherd_pcb_v2.2_Copper_Sig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]
2021-06-27 pick and place data
    [Pick Place for shepherd_pcb_v2.2_emu_only.csv, Pick Place for shepherd_pcb_v2.2_rec_emu.csv]
2021-07-17 calibration data
2021-09-21 Update dev_log_sys_stats.py
    fix logging of subprocesses -> h5 only wants threads
2021-12-01 design-files for cape v2.3
    [2021-12-01 Bestellung Mouser Digikey.xlsx, Bill of Materials-shepherd_v2.3_inventar.xlsx, Mouser-Bestellung.xlsx, shepherd_pcb_v2.3c_Copper_Signal_1.gbr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]
2021-12-01 small changes
    [2021-12-01 Bestellung Mouser Digikey.xlsx, 2021-12-02 Bestellung Mouser Digikey.xlsx, Bill of Materials-shepherd_v2.3_inventar.xlsx]
2022-01-18 big doc update
    [beaglebone_pinout_concept.xlsx]
2022-01-18 next steps
    [2022-01-19 - Mouser order.xls]
2022-01-20 BOM orders
    [2021-12-02 Bestellung Mouser Digikey.xlsx, 2022-01-19 - Mouser order.xls, Bill of Materials-shepherd_v2.3_inventar.xlsx]
2022-03-02 pcb progress
2022-03-22 hw update
    [BOM_missing_parts_v2.xlsx, BOM_missing_parts_v3.xlsx, Bill of Materials-shepherd_dev_io.xlsx, Bill of Materials-shepherd_v2.xlsx]
2022-08-01 finalized cape v2.4
    [Bill of Materials-shepherd_v2.xlsx, shepherd_pcb_v2.4_Assembly_Notes.gbr, shepherd_pcb_v2.4_Copper_Signal_1.gbr, shepherd_pcb_v2.4_Copper_Signal_2.gbr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]
2022-08-03 small revision to fix some BOM-Errors
    [BOM_Print_Labels.xlsx, Bill of Materials-shepherd_v2.4.xlsx, Bill of Materials-shepherd_v2.xlsx, shepherd_pcb_v2.4_Assembly_Notes.gbr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]
2022-08-03 Adapt to Mouser-Stock -> Avoid 350um-Pitch Part
    now its >= 500 um Pitch again
    [shepherd_pcb_v2.4_Assembly_Notes.gbr, shepherd_pcb_v2.4_Copper_Signal_1.gbr, shepherd_pcb_v2.4_Copper_Signal_2.gbr, shepherd_pcb_v2.4_Copper_Signal_Bot.gbr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]
2022-08-04 finish order-details
    [shepherd_v2.4 - bestand.xlsx, shepherd_v2.4_Bill of Materials_packliste.xlsx]
2022-08-11 Update shepherd_v2.4_Bill of Materials_packliste.xlsx
    [shepherd_v2.4_Bill of Materials_packliste.xlsx]
2022-08-11 Update List of BB MAC-Addresses.ods
    [List of BB MAC-Addresses.ods]
2022-09-23 Cape PCB - add missing layers
    [shepherd_pcb_v2.4_Assembly_Notes.gbr, shepherd_pcb_v2.4_Copper_Signal_1.gbr, shepherd_pcb_v2.4_Copper_Signal_2.gbr, shepherd_pcb_v2.4_Copper_Signal_3.gbr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]
2022-11-25 board eval
2023-03-14 shepherd cape v2.4c
    [Bill of Materials-shepherd_v2.4.xlsx, shepherd_pcb_v2.4_Assembly_Notes.gbr, shepherd_pcb_v2.4_Copper_Signal_1.gbr, shepherd_pcb_v2.4_Copper_Signal_2.gbr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]
2023-04-17 add new power-board
    [Bill of Materials-shepherd_power.xlsx, board_NPTH_Drill.gbr, board_PTH_Drill.gbr, target_c_Copper_Signal_Bot.gbr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]
2023-04-17 add nRF-FRAM-Target
    [40 - MouserBom.xls, Bill of Materials-nRF_FRAM_Target.xlsx, target_c_Copper_Signal_1.gbr, target_c_Copper_Signal_2.gbr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]
2023-04-17 add nRF52-Target v2.3
    [Bill of Materials-shepherd_target_nRF.xlsx, target_nRF_Copper_Signal_1.gbr, target_nRF_Copper_Signal_2.gbr, target_nRF_Copper_Signal_Bot.gbr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]
2023-05-15 review pcbs
2023-08-24 move current pcb-data to main-project
    [40 - MouserBom.xls, Bill of Materials-nRF_FRAM_Target.xlsx, Bill of Materials-shepherd_target_nRF.xlsx, target_c_Copper_Signal_1.gbr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]
2023-08-24 rename pcb-dir
    [2021-04-10_Cost_of_Production.ods, 2021-12-02 Bestellung Mouser Digikey.xlsx, 2022-01-19 - Mouser order.xls, BOM_Print_Labels.xlsx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]
2023-09-10 deployment tests
    [Target_pre-deployment-tests.xlsx]
2023-09-10 move relevant testbed data
    [Target_pre-deployment-tests.xlsx]
2023-09-12 finish case design
2023-09-17 refactor case
2023-09-17 add newest pcb versions
    [Bill of Materials-shepherd_power.xlsx, Bill of Materials-shepherd_v2.xlsx, board_Assembly_Notes.gbr, board_Bottom_Designator.gbr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]
2023-09-17 documentation on new PCBs
2023-09-17 Update shepherd_v2.4 - bestand.xlsx
    [shepherd_v2.4 - bestand.xlsx]
2023-09-21 doc updates
    [Target_pre-deployment-tests.xlsx, ethernet_MAC_addresses_bbones.ods, ethernet_ports_cfaed.ods]
2023-09-25 update testbed-data
    [Cape_pre-deployment-tests.xlsx]
2023-09-25 add latest performance analysis
    [49_sw_py_speed_optimizations_profile_pydantic22.csv, 49_sw_py_speed_optimizations_profile_pydantic24.csv]
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2024-02-05 move loose parts to doc
    [2020-12-15_rf_measurements.ods]
2024-02-07 move hardware-data to main-repo
    [2021-04-10_Cost_of_Production.ods, 2021-12-02 Bestellung Mouser Digikey.xlsx, 2022-01-19 - Mouser order.xls, BOM_Print_Labels.xlsx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]
2024-02-08 latest changes
    [leveltranslator isolated.SchDoc]
2024-02-15 more refactoring
    [49_sw_py_speed_optimizations_profile_pydantic22.csv, 49_sw_py_speed_optimizations_profile_pydantic24.csv]
2024-10-24 add measurements
    [cap1_s1_chg.csv, cap1_s1_dis.csv, cap1_s2_chg.csv, cap1_s2_dis.csv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]
2024-10-25 add pure ivcurves
    [solar-iv-1100mA.ivcurve.csv, solar-iv-1100mA.ivcurve.raw.csv, solar-iv-400mA.ivcurve.csv, solar-iv-400mA.ivcurve.raw.csv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]
2024-10-26 shorten ivcurves
    [solar-iv-1100mA.ivcurve.csv, solar-iv-400mA.ivcurve.csv, solar-iv-900mA.ivcurve.csv]
2024-10-31 add new capacitor measurements
    [cap1_selfdis_charge010s.csv, cap1_selfdis_charge010s_check.csv, cap1_selfdis_charge020s.csv, cap1_selfdis_charge050s.csv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]
2024-11-08 add actual data
    [boost_lut_processed.csv, boost_lut_raw_vout2.500.csv, boost_lut_raw_vout2.750.csv, boost_lut_raw_vout3.000.csv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]
2024-11-09 add missing data
    [LED_003pc.ivcurve.csv, LED_003pc.pru_util.csv, LED_003pc.sys_util.csv, LED_004pc.ivcurve.csv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]
2024-11-09 refactor paths
    [LED_003pc.ivcurve.csv, LED_003pc.pru_util.csv, LED_003pc.sys_util.csv, LED_004pc.ivcurve.csv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]
2024-11-22 update target test-results
    [Target_v10_pre-deployment-tests.xlsx, Target_v13_pre-deployment-tests.xlsx]
2024-11-22 move data to separate repo
    https://github.com/orgua/bq_characteristics
    [boost_lut_processed.csv, boost_lut_raw_vout2.500.csv, boost_lut_raw_vout2.750.csv, boost_lut_raw_vout3.000.csv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]
2024-12-08 add profiles of parts
    [profiler_smu_cap_1nF_0402_C0G.csv, profiler_smu_hrv_V_HRV_at_5V.csv, profiler_smu_hrv_diodes.csv, profiler_smu_solar_power.csv]
2025-03-11 add profiler data
    [profile_analysis.csv, profile_analysis_2022_02_24.xlsx, profile_analysis_emulator.xlsx, profile_analysis_harvester.ods]
2025-03-11 add timesync measurements dresden
    [000_BBBlack_as_ptp_server_18us_path_delay.csv, 000_one_cm4.csv, 001_.csv, 001_baseline.csv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]
2025-04-02 update doc
    [Cape25d_pre-deployment-tests.xlsx, Target_v13e_pre-deployment-tests.xlsx]
